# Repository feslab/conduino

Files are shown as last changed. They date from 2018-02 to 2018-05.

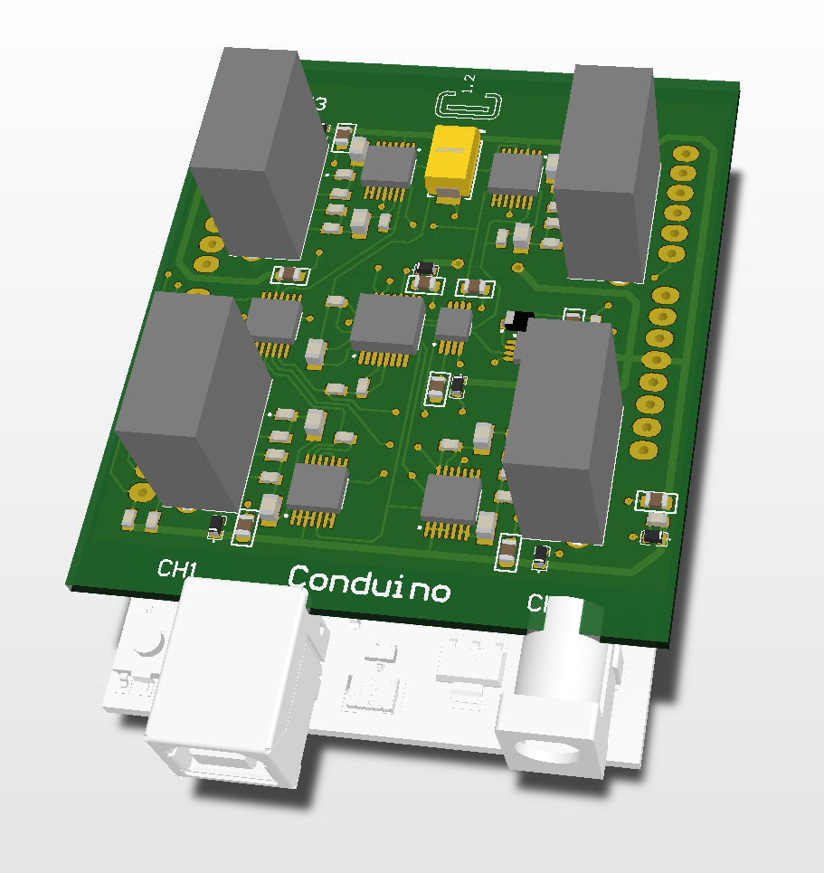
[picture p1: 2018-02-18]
hardware/Cond2.png

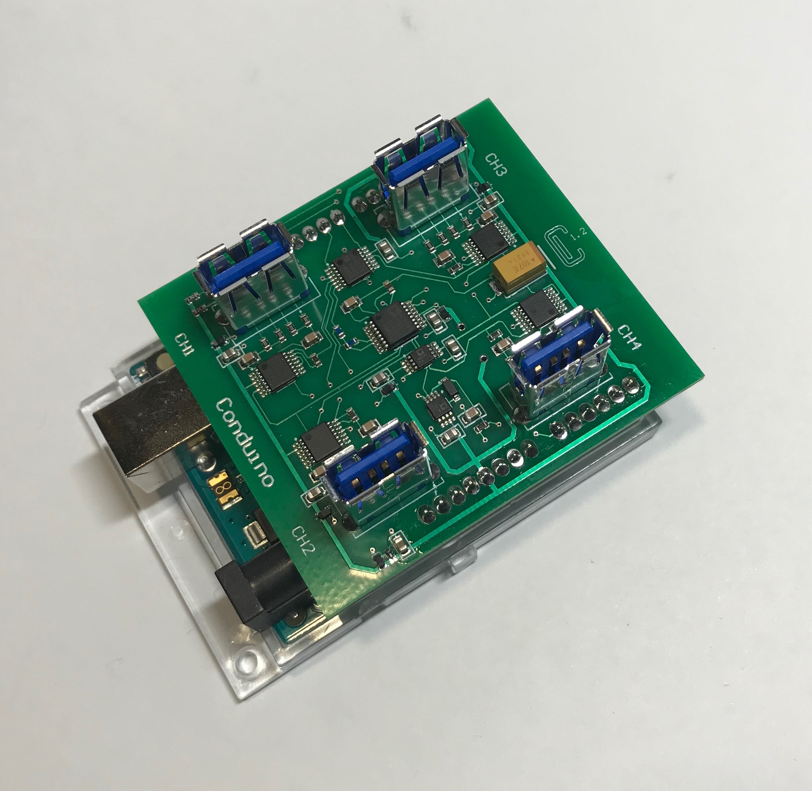
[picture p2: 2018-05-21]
hardware/AssemblyPic2.jpg

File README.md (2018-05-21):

# Conduino 1.2

For any questions or comments please contact 
[Marco Carminati](http://www.deib.polimi.it/eng/people/details/126878) or [Paolo Luzzatto-Fegiz](https://feslab.me.ucsb.edu/people/paolo-luzzatto-fegiz) 

If you use a Conduino in your work, please include the citation:
Marco Carminati, Paolo Luzzatto-Fegiz, Conduino: Affordable and high-resolution multichannel water conductivity sensor using micro USB connectors, In Sensors and Actuators B: Chemical, Volume 251, 2017, Pages 1034-1041, ISSN 0925-4005, https://doi.org/10.1016/j.snb.2017.05.184.

The repository contains the following files:

Hardware:

- Conduino_Gerber:  Gerber-format design files to prepare a PCB;
- AssemblyFile.png: Assembly overview;
- Cond1.png, Cond2.png: 3D (approximate) drawings of completed Conduino 1.2;
- Schematic Conduino 1.2.pdf: Schematics for the electronic design;
- BOM_PartType-Conduino.xlsx: Bill of materials;
- License.md: CC BY 4.0 license description.

Software:

- Matlab: Files for operation through a Matlab Script;
    - Firmware_Conduino_Matlab: Arduino Sketch;
    - ConduinoMultichannel.m: Marlab script, suitable for both Mac or PC;
- Terminal: Files for operation through a serial port terminal;
    - Firmware_Conduino_Terminal: Arduino Sketch;
    - Termite.exe: RS232 serial port terminal for PC, requires no installation see https://www.compuphase.com/software_termite.htm;
    - termite.cat: place in the same folder as Termite.exe;
    - Settings Termite.pdf: Settings for Termite, or similar serial port terminals.
- _Software_for_older_Conduinos_1p0-1p1: versions for older Conduinos;

Conduino 1.2 differs from the Conduino 1.0 described in the 2017 paper:

- Parts that were needed exclusively for the 4-electrode circuit have been removed. This revision substantially simplifies probe design, and reduces complexity. In our tests so far there has been no need to switch from 2-electrode to 4-electrode measurement;
- The overall layout has been revised for a more compact design, and to eliminate a slight kinematic conflict between Ch.4 and the Arduino Uno's USB port.

Areas of ongoing work on Conduino 1.2:

- There is currently no enclosure design. If you design an enclosure, we would be happy to add the CAD file to this repository, of course with attribution;
- If using more than one Conduino (that is, in applications where more than four sensors are needed) in the same tank, interference may develop. We are working to address this, most likely with a software update. There are no interference issues between the four sensors operated by a single Conduino.

If you are looking for an assembled system for purchase, please contact conduino@gmail.com.

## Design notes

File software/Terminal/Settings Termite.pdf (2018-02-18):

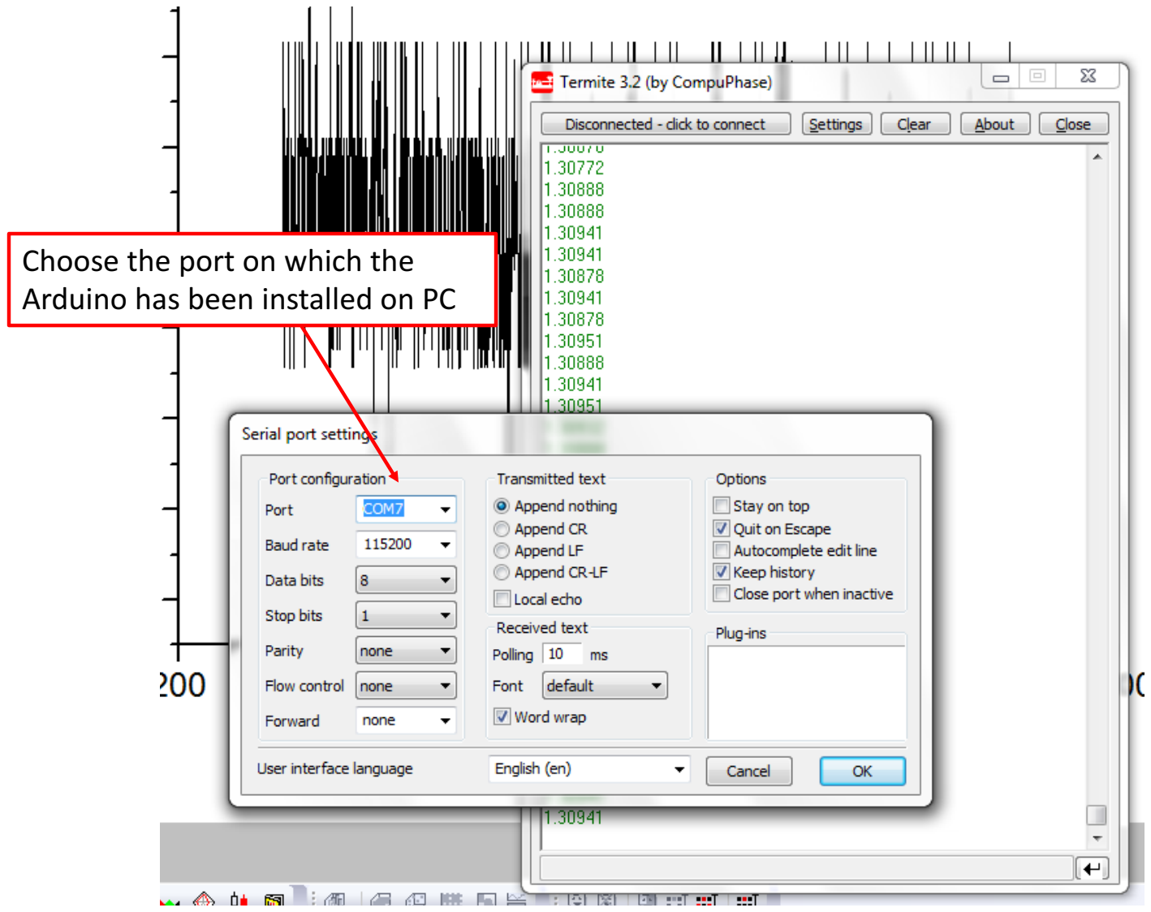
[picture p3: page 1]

Choose the port on which the Arduino has been installed on PC

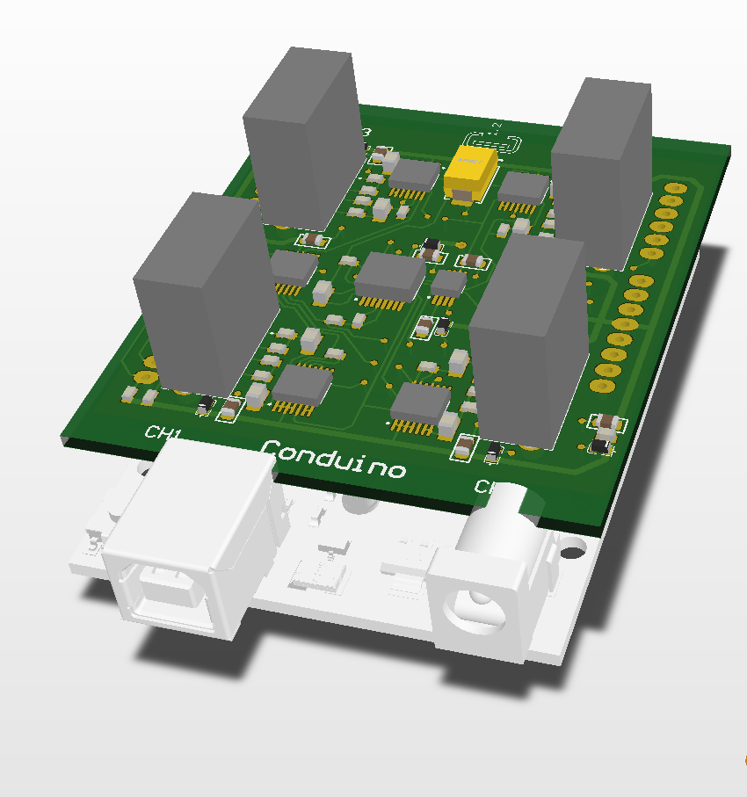
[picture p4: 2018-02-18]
hardware/Cond1.png

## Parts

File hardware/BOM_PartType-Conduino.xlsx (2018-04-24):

Designator | Comment | Quantity | Description | Manufacturer | Manufacturer PN (w. link) | Case/Package | Unitary cost | Tot cost
C1, C4, C7, C12, C17, C20, C26 | 10u | 7 | Tantalum Capacitors - Solid SMD 6.3V 10uF 20% 0603 ESR= 6 Ohms | AVX | F980J106MMA (https://www.mouser.com/ProductDetail/AVX/F980J106MMA?qs=sGAEpiMZZMuEN2agSAc2puC4lhRhLeoltAeW2dBMmdg=) | 0603 | 0.72 | 5.04
C2, C5, C6, C10, C13, C18, C19, C21, C23, C27 | 100n | 10 | Multilayer Ceramic Capacitors MLCC - SMD/SMT 0.1uF 50V X7R 20% 0805 Flx AEC-Q200 | Taiyo Yuden (https://www.mouser.it/taiyo-yuden) | UMJ212BB7104MGHT (https://www.mouser.it/ProductDetail/Taiyo-Yuden/UMJ212BB7104MGHT) | 0805 | 0.44 | 4.41
C3, C11, C14, C15, C16, C22, C24, C25, C28, C29 | 1u | 10 | Multilayer Ceramic Capacitors MLCC - SMD/SMT 0805 25V 1.00uF X8R 20% Soft Term | TDK (https://www2.mouser.com/tdk) | C2012X8R1E105M125AE | 0805 | 0.49 | 4.92
C8 | 100pF | 1 | Multilayer Ceramic Capacitors MLCC - SMD/SMT | Murata Electronics (https://www2.mouser.com/murataelectronics/) | GCM0335C1E101GA16D | 0603 | 0.10 | 0.10
C9 | 100u | 1 | Capacitor, Tantalum, 100 uF, +/- 10%, -55 to 125 degC, 2-Pin SMD, RoHS, Tape and Reel | AVX | TPME107K025R0045 | 7343 | 6.97 | 6.97
D1 | 1N4148 | 1 | Diodes - General Purpose, Power, Switching SMT Fast Switching Diode | Diodes Incorporeted | 1N4148WQ-7-F | SOD-123 | 0.20 | 0.20
J2, J3, J4, J5 | Connector | 4 | Recept Assy, Vertical, 4 Position, Thru-Hole, Type A USB, RoHS, Tray | TE Connectivity | 1734366-3 (https://www2.mouser.com/ProductDetail/TE-Connectivity-AMP/1734366-3) |  | 0.84 | 3.37
R1, R2, R6, R7, R8, R9, R11, R12, R16, R17, R20, R21, R22, R23, R25, R26 | 0 | 16 | Thick Film Resistors - SMD 1/10Watt 0ohms Commercial Use | Vishay | CRCW06030000Z0EBC (https://eu.mouser.com/ProductDetail/Vishay/CRCW06030000Z0EBC) | 0603 | 0.10 | 1.60
R3, R4 | 10k | 2 | Thick Film Resistors - SMD 1/10W 10K Ohm .1% 75V | Yageo | RE0603BRE0710KL (https://eu.mouser.com/ProductDetail/Yageo/RE0603BRE0710KL?qs=sGAEpiMZZMtlubZbdhIBIKyAF7UHeJ2ZIxtSvRbq3ww%3d) | 0603 | 0.36 | 0.72
R5, R10, R19, R24 | 180 | 4 | Thick Film Resistors - SMD 0603 Resistor 0.5% 50ppm 180Ohm | Panasonic | ERJ-3RBD1800V (https://www2.mouser.com/ProductDetail/Panasonic/ERJ-3RBD1800V) | 0603 | 0.12 | 0.48
R13 | 2.5k | 1 | Thin Film Resistors - SMD .5watt 2.5Kohm 25ppm 0.1% 0603 SMD | Vishay | PCAN0603E2501BST5 (https://www2.mouser.com/ProductDetail/Vishay-Thin-Film/PCAN0603E2501BST5) | 0603 | 0.94 | 0.94
R14, R15 | 20k | 2 | Thin Film Resistors - SMD .250W 20Kohms .5% 0603 25ppm Hi Power | Vishay | MCT0603PD2002DP500 (https://www2.mouser.com/ProductDetail/Vishay-BC-Components/MCT0603PD2002DP500) | 0603 | 0.57 | 1.14
R18 | 1k | 1 | Thick Film Resistors - SMD 0603 Resistor 0.5% 50ppm 1.1KOhm | Panasonic | ERJ-3RBD1101V (https://www2.mouser.com/ProductDetail/Panasonic/ERJ-3RBD1101V) | 0603 | 0.12 | 0.12
U1, U3, U6, U8 | Op amp | 4 | 3 Channel Single-Supply Operation Operational Amplifier, 220 MHz BW, 170 V/us SR, Industrial, 14-pin SOP (RU-14), Tube | Analog Devices | ADA4891-3ARUZ-R7 (https://www2.mouser.com/ProductDetail/Analog-Devices/ADA4891-3ARUZ-R7?qs=sGAEpiMZZMv9Q1JI0Mo%2ftbQOvCFTKx7r) | TSSOP | 2.55 | 10.20
U2 | Voltage reg. | 1 | Ultralow Noise, LDO XFET Voltage Reference with Current Sink and Source, 2.5 V Output, 3 to 18 V Supply, Industrial, 8-pin SOP (RM-8), Tube | Analog Devices | ADR441ARMZ-REEL7 | MSOP | 6.25 | 6.25
U4 | Imp measure | 1 | 1 MSPS, 12-Bit Impedance Converter, Network Analyzer, Serial, RS-16, 77 Tube, Pb-Free | Analog Devices | AD5933YRSZ | SSOP | 33.64 | 33.64
U5 | Mux | 1 | 1 pC Charge Injection, 100 pA Leakage CMOS 3 V / 5 V / +/-5 V 4-Channel Multiplexer, -40 to 125 degC, 14-pin SOP (RU-14), Tube | Analog Devices | ADG604YRUZ-REEL7 (https://www2.mouser.com/ProductDetail/Analog-Devices/ADG604YRUZ-REEL7) | TSSOP | 4.96 | 4.96
U7 | Op amp | 1 | Single Channel Rail-to-Rail Operational Amplifier, 1.9 MHz BW, 3 V/us SR, Industrial, 8-pin SOP (RM-8), Tube | Analog Devices | AD820ARMZ-R7 (https://www2.mouser.com/ProductDetail/Analog-Devices/AD820ARMZ-R7?qs=sGAEpiMZZMv9Q1JI0Mo%2ftYvoW7ReYAMC) | MSOP | 4.80 | 4.80
 |  |  |  |  |  |  | TOT | 89.87

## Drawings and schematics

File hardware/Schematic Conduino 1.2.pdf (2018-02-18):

Arduino | Channel1 | Channel2

# Channel

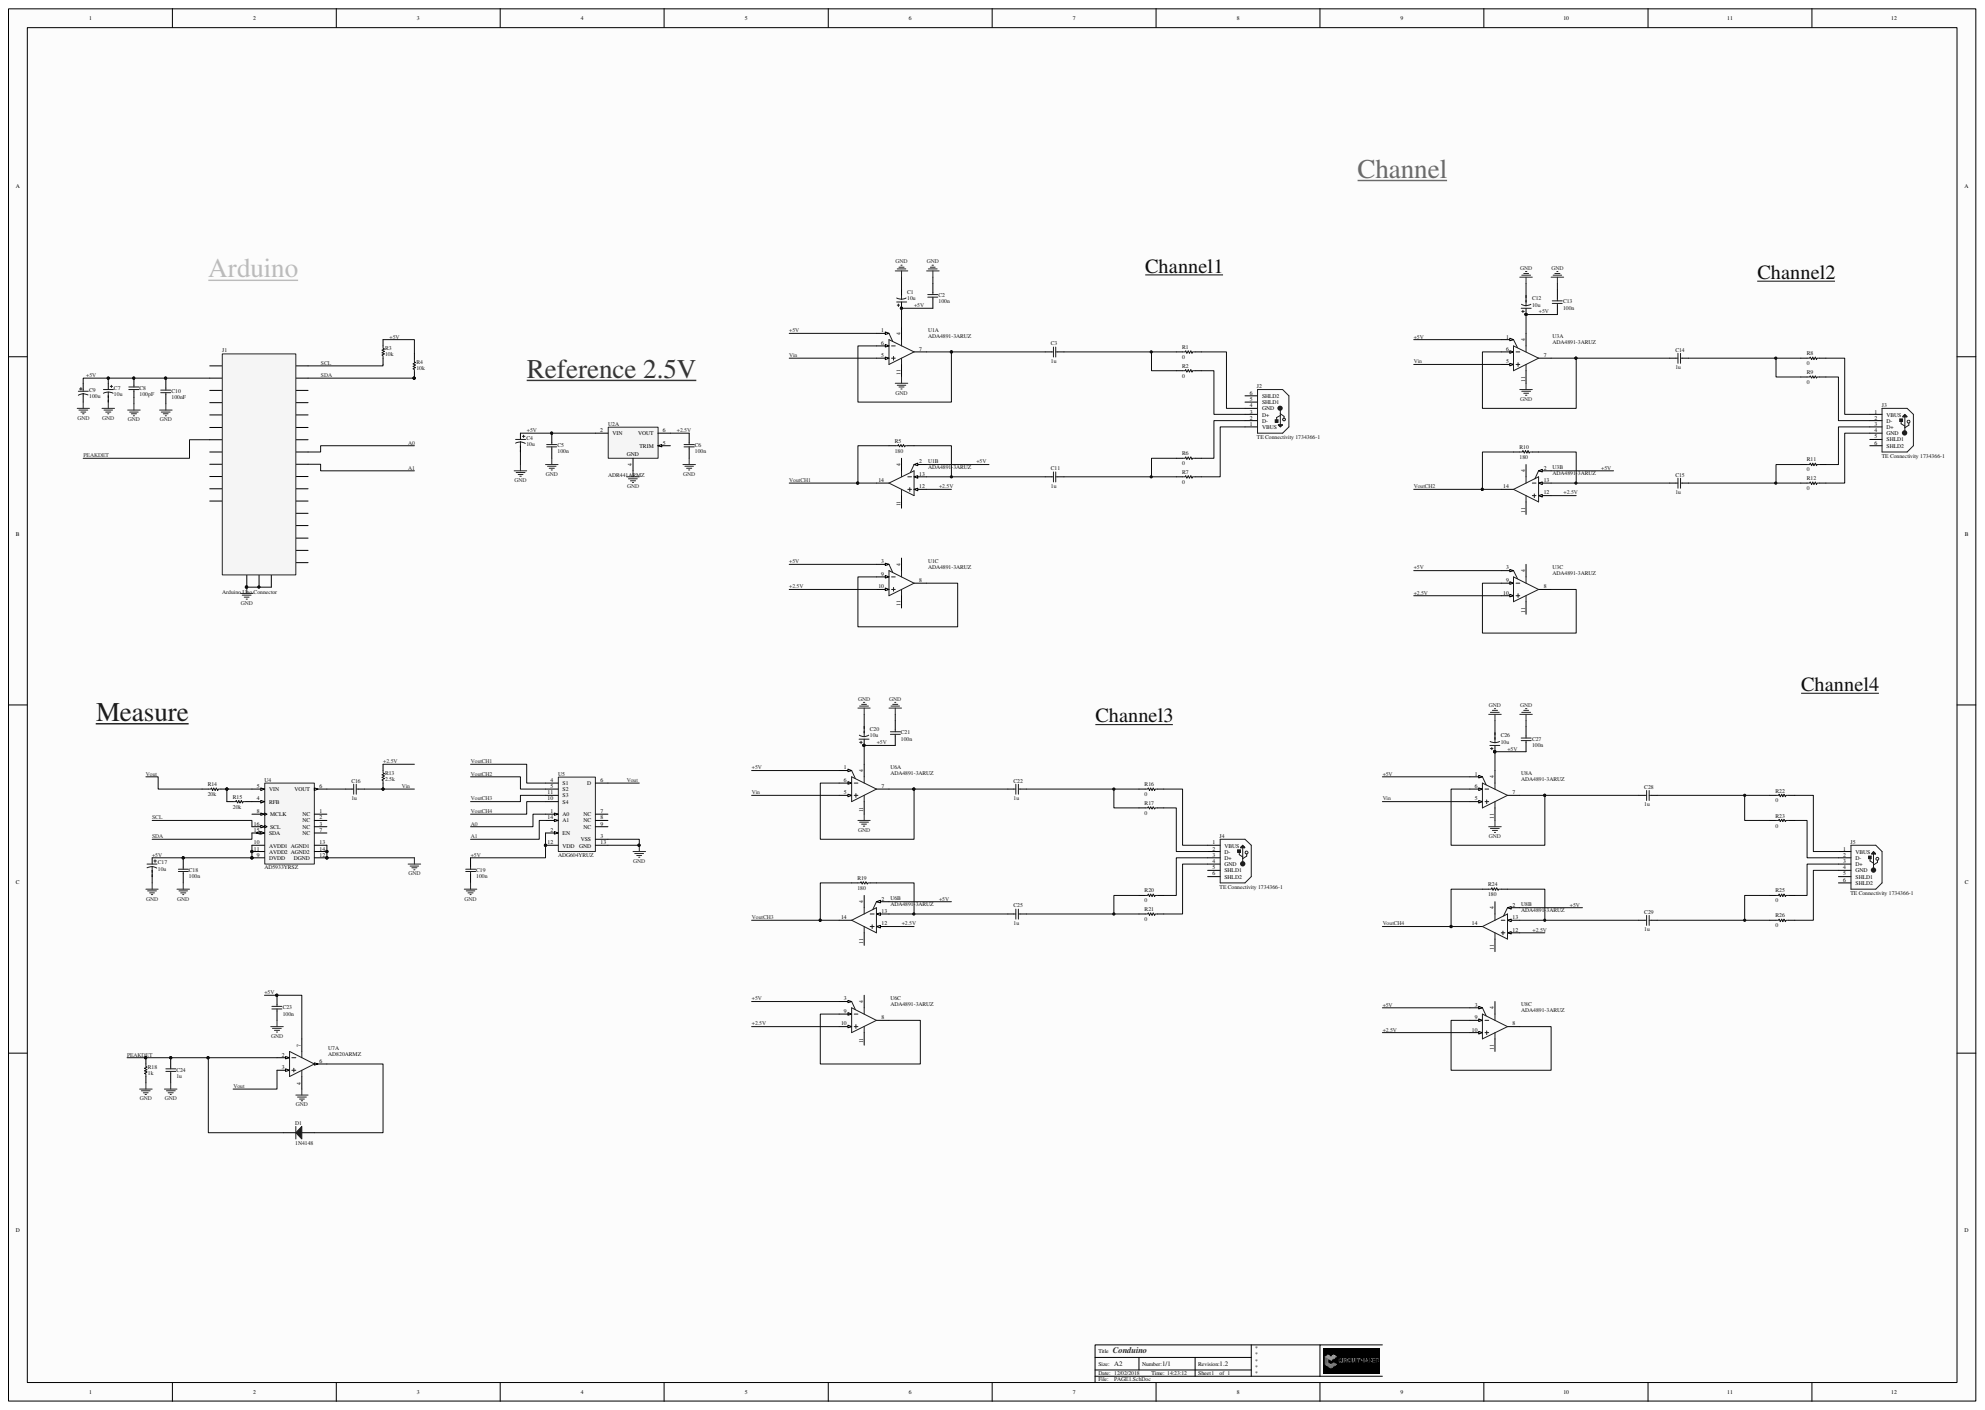
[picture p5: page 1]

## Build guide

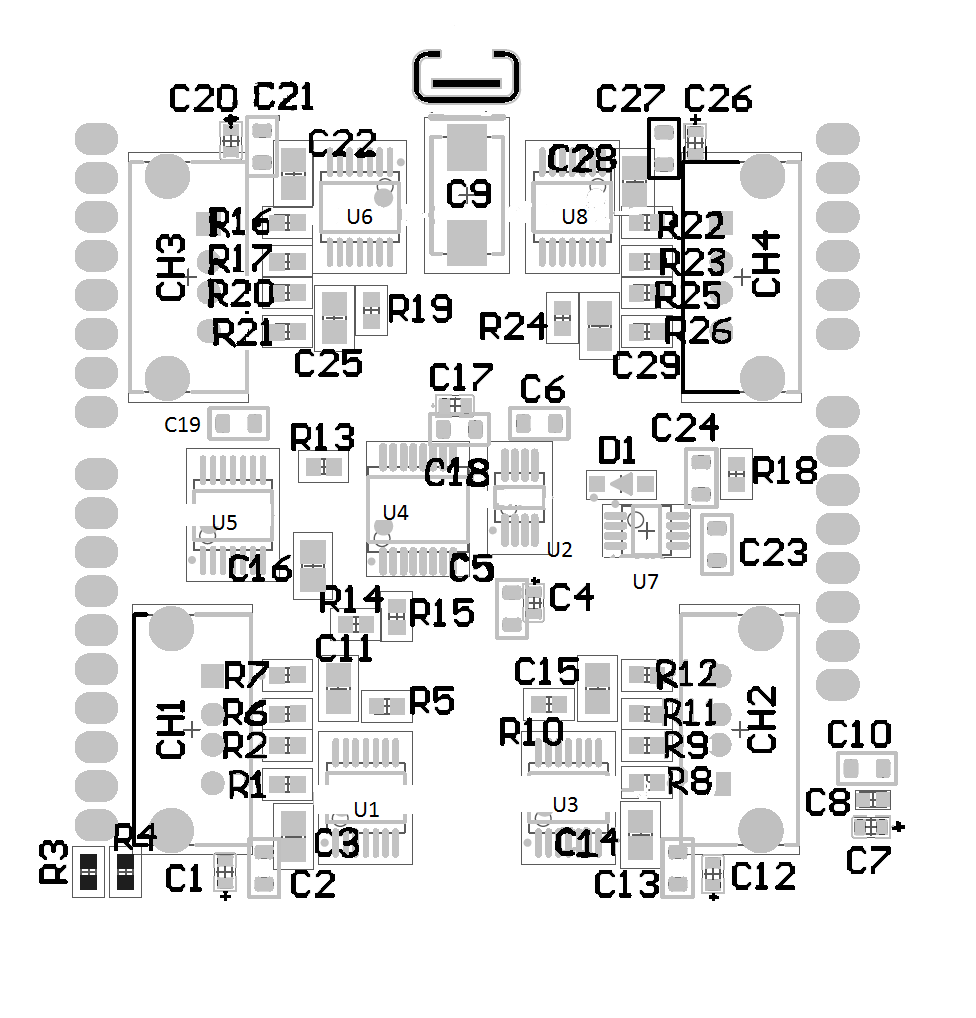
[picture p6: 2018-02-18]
hardware/Assemblyfile.png

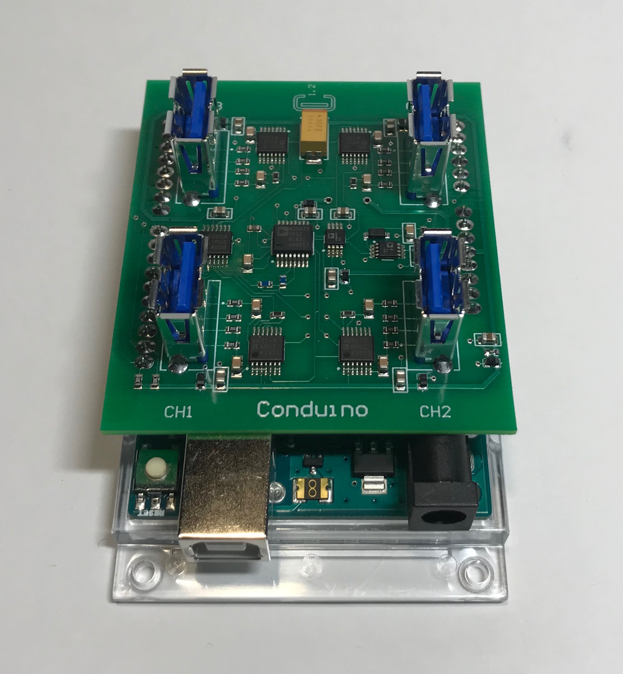
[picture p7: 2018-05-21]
hardware/AssemblyPic1.jpg

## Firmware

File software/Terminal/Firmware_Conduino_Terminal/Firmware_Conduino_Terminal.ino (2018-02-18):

#include <Wire.h>

// The user must calibrate the AD5933 system for a known impedance range to determine the gain factor

#define AD5933_ADDR 0x0D
#define AD5245_ADDR 0x2D //B0101101; // << assumes AD0 tied to VCC

const float CLOCK_SPEED = 16.776 * pow(10, 6); // AD5933 has internal clock of 16.776 MHz

const int CONTROL_REGISTER[2] =                    { 0x80, 0x81       }; // see mapping below
const int START_FREQUENCY_REGISTER[3] =            { 0x82, 0x83, 0x84 }; // 24 bits for start frequency
const int FREQ_INCREMENT_REGISTER[3] =             { 0x85, 0x86, 0x87 }; // 24 bits for frequency increment
const int NUM_INCREMENTS_REGISTER[2] =             { 0x88, 0x89       }; //  9 bits for # of increments
const int NUM_SETTLING_CYCLES_REGISTER[2] =        { 0x8A, 0x8B       }; //  9 bits + 1 modifier for # of settling times
const int STATUS_REGISTER[1] =                     { 0x8F             }; // see mapping below
const int TEMPERATURE_DATA_REGISTER[2] =     { 0x92, 0x93       }; // 16-bit, twos complement format
const int REAL_DATA_REGISTER[2] =                  { 0x94, 0x95       }; // 16-bit, twos complement format
const int IMAG_DATA_REGISTER[2] =                  { 0x96, 0x97       }; // 16-bit, twos complement format

// control register map (D15 to D12)
const int DEFAULT_VALUE =                 B0000; // initial setting
const int INITIALIZE =                    B0001; // excite the unknown impedance initially
const int START_SWEEP =             B0010; // begin the frequency sweep
const int INCREMENT =                     B0011; // step to the next frequency point
const int REPEAT =                        B0100; // repeat the current frequency point measurement
const int MEASURE_TEMP =                  B1001; // initiates a temperature reading
const int POWER_DOWN =                    B1010; // VOUT and VIN are connected internally to ground
const int STANDBY =                       B1011; // VOUT and VIN are connected internally to ground

const int BLOCK_WRITE = B1010000;
const int BLOCK_READ =  B1010001;
const int ADDRESS_PTR = 0xB0;// B1011000;

const int validTemperatureMeasurement =  1;
const int validImpedanceData =           2;
const int frequencySweepComplete =       4;

//functions declarations
int checkStatus();
boolean measureTemperature();
byte frequencyCode(float, int);
boolean setStartFrequency(float);
boolean setFrequencyIncrement(float);
boolean setNumberOfIncrements(int);
boolean setNumberOfSettlingTimes(int);
void measureImpedance();
void configureAD5933(int, float, float, int);
int getByte(int);
boolean setByte(int, int);
boolean setControlRegister(int);
void setChannel(int);

boolean setControlRegister2();


const int ledPin = 13;

int reading = 0;
byte rxByte;
int number;
char FirstChar[1];
char SecondChar[1];

int e = 0;
int y;
int ch;
int u;

// Arduino setup:

// D8 = MUX1
// D9 = MUX0


const int mux1 = 8;
const int mux0 = 9;

int channelNumber = 0;

void setup()
{
  Wire.begin();
  Serial.begin(115200);

  pinMode(ledPin, OUTPUT);

  pinMode(mux1, OUTPUT);
  pinMode(mux0, OUTPUT);


  configureAD5933(2, // number of settling times
                  1 * pow(10, 5), // start frequency (Hz)
                  1 * pow(10, 4), // frequency increment (Hz)
                  0); // number of increments

  setControlRegister2();

}

void loop()
{
      y = 2;
      Serial.print("Specify number of samples:    ");
      Serial.setTimeout(10);
      
          while (y == 2) {

              if (Serial.available()) {
                y = 1;
               number = Serial.parseInt();
               Serial.println(number);
              }
           }
          
      Serial.println("Start reading..............");
      Serial.println(" ");
      Serial.println("  Ch1               Ch2               Ch3               Ch4  ");
      digitalWrite(ledPin, HIGH);
      delay(10);

      measureImpedance();

      digitalWrite(ledPin, LOW);
      delay(1000);
}







// message sequence:
// to set the memory address:
// 1. slave address
// 2. pointer command
// 3. register address to point to

// to write data (address already set):
// 1. slave address
// 2. block write
// 3. number bytes write
// 4. byte 0, byte 1, byte 2, etc.

// to read data (address is already set):
// 1. slave address with read bit high
// 2. register data is returned

// to read a block of data (address is already set):
// 1. slave address
// 2. block read
// 3. number of bytes
// 4. slave address (read bit high)
// 5. byte 0, byte 1, byte 2, etc.


// control register map (D10 to D9)
// ranges = {2.0 V p-p, 200 mV p-p, 400 mV p-p, 1.0 V p-p}
const int OUTPUT_VOLTAGE[4] = {
  B00, B01, B10, B11
};

// control register map (D11, D8 to D0)
// D11 = no operation
// D8 = PGA gain (0 = x5, 1 = x1) // amplifies the response signal into the ADC
// D7 = reserved, set to 0
// D6 = reserved, set to 0
// D5 = reserved, set to 0
// D4 = reset // interrupts a frequency sweep
// D3 = external system clock, set to 1; internal system clock, set to 0
// D2 = reserved, set to 0
// D1 = reserved, set to 0
// D0 = reserved, set to 0

// number of increments register
// 0x88: D15 to D9 -- don't care
// 0x89: D8 -- number of increments bit 1
// 0x89: D7 to D0 -- number of increments bits 2 through 9; 9-bit integer number stored in binary format

// number of settling times
// 0x8A: D15 to D11 -- don't care
// 0x8A: D10 to D9 -- 2-bit decode
//        0 0 = default
//        0 1 = # of cycles x 2
//        1 0 = reserved
//        1 1 = # of cycles x 4
// 0x8A: D8 -- MSB number of settling times
// 0x8B: D7 to D0 -- number of settling times; 9-bit integer number stored in binary format

// status register


int checkStatus() {
  return (getByte(STATUS_REGISTER[0]) & 7);
}

boolean measureTemperature() {

  setControlRegister(MEASURE_TEMP);

  delay(10); // wait for 10 ms

  if (checkStatus() & 1 == validTemperatureMeasurement) {

    // temperature is available
    int temperatureData = getByte(TEMPERATURE_DATA_REGISTER[0]) << 8;
    temperatureData |= getByte(TEMPERATURE_DATA_REGISTER[1]);
    temperatureData &= 0x3FFF; // remove first two bits

    if (temperatureData & 0x2000 == 1) { // negative temperature

      temperatureData -= 0x4000;
    }

    temperatureData /= 32;

    Serial.print("Current temperature is ");
    Serial.print(temperatureData);
    Serial.println(" degrees Celsius.");

    setControlRegister(POWER_DOWN);

    return true;

  } else {
    return false;
  }
}

// start frequency and frequency increment formula:
byte frequencyCode(float freqInHz, int byteNum)
{
  long value = long((freqInHz / (CLOCK_SPEED / 4)) * pow(2, 27));

  byte code[3];

  code[0] = (value & 0xFF0000) >> 0x10;
  code[1] = (value & 0x00FF00) >> 0x08;
  code[2] = (value & 0x0000FF);

  return code[byteNum];
}

boolean setStartFrequency(float freqInHz)
{



  boolean statusValue;

  for (int n = 0; n < 3; n++) {
    statusValue = setByte(START_FREQUENCY_REGISTER[n], frequencyCode(freqInHz, n));
  }

  return statusValue;

}


boolean setFrequencyIncrement(float freqInHz)
{


  boolean statusValue;

  for (int n = 0; n < 3; n++) {
    statusValue = setByte(FREQ_INCREMENT_REGISTER[n], frequencyCode(freqInHz, n));
  }

  return statusValue;

}


boolean setNumberOfIncrements(int n)
{


  boolean i2cStatus;

  int numIncrements = min(n, 511);

  i2cStatus = setByte(NUM_INCREMENTS_REGISTER[0], numIncrements >> 8);
  i2cStatus = setByte(NUM_INCREMENTS_REGISTER[1], numIncrements & 255);

  return i2cStatus;
}


boolean setNumberOfSettlingTimes(int n)
{



  int decode;
  int numSettlingTimes = min(n, 2047);

  if (n > 1023) {
    decode = 3;
    numSettlingTimes /= 4;
  }
  else if (n > 511) {
    decode = 1;
    numSettlingTimes /= 2;
  }
  else {
    decode = 0;
    numSettlingTimes = n;
  }

  boolean i2cStatus;

  i2cStatus = setByte(NUM_SETTLING_CYCLES_REGISTER[0], (numSettlingTimes >> 8) + (decode << 1));
  i2cStatus = setByte(NUM_SETTLING_CYCLES_REGISTER[0], numSettlingTimes & 255);

  return i2cStatus;

}



void measureImpedance() {


  int real = 0;
  int imag = 0;
  e = 0;
  //0.Inizialize bit D11,D10,D9,D8
  setControlRegister2();

  // 1. place AD5933 in standby mode
  setControlRegister(STANDBY);

  // 2. initialize with start frequency
  setControlRegister(INITIALIZE);


  // 3. start frequency sweep
  setControlRegister(START_SWEEP);

  int rxcontrol = getByte(CONTROL_REGISTER[0]);

      real = getByte(REAL_DATA_REGISTER[0]) << 8;
      real |= getByte(REAL_DATA_REGISTER[1]);
    
        imag = getByte(IMAG_DATA_REGISTER[0]) << 8;
        imag |= getByte(IMAG_DATA_REGISTER[1]);
    

  // start array:



  // 4. poll status register until complete
  //while (checkStatus() < validImpedanceData) {
  //}
  for (u = 0; u < number; u++) { 
    
    for ( ch=1; ch < 5 ; ch++) {

      setChannel(ch);
    setControlRegister(REPEAT);
      delay(6);

      // 5. read values
      real = getByte(REAL_DATA_REGISTER[0]) << 8;
      real |= getByte(REAL_DATA_REGISTER[1]);

        if (real > 0x7FFF) { // negative value
          real &= 0x7FFF;
          real -= 0x10000;
        }
    
        imag = getByte(IMAG_DATA_REGISTER[0]) << 8;
        imag |= getByte(IMAG_DATA_REGISTER[1]);
    
        if (imag > 0x7FFF) { // negative value
          imag &= 0x7FFF;
          imag -= 0x10000;
        }
    
        double magnitude = sqrt(pow(double(real), 2) + pow(double(imag), 2));
        double gain = 2.3 * pow(10, -10); //calibrated with 220kOhm resistor on 1/3/12
    
        double impedance = 1 / (gain * magnitude * 45400 / 1.63);
    
        double phase = atan(double(imag) / double(real)) * 360 / (2 * 3.14) + 47;
    
        double conductivity = 129 / impedance;
    
    
        //Serial.print("Conductivity: ");
        Serial.print(conductivity, 4);
        Serial.print("            ");
    
    
        //  double limit = analogRead(A0);
        //   limit *=5;
        //   limit /=1023;
        //   Serial.print(limit);
        //   Serial.print(" V ");
        //   Serial.println("; ... ");
    
    
    
    
        //Serial.println(" ");


  }
  Serial.println(" ");
  }




  // 8. power-down mode
  setControlRegister(POWER_DOWN);


}


void configureAD5933(int settlingTimes, float startFreq, float freqIncr, int numIncr)
{
  setNumberOfSettlingTimes(settlingTimes);
  setStartFrequency(startFreq);
  setFrequencyIncrement(freqIncr);
  setNumberOfIncrements(numIncr);

}






// How to write or read a byte:
// 1. master device asserts a start condition on SDA
// 2. master sends the 7-bit slave address followed by the write bit (low)
// 3. addressed slave device asserts an acknowledge on SDA
// 4. The master send a register address or pointer command code (1011 0000)
// 5. the slave asserts an acknowledge on SDA
// 6. the master sends a data byte or register address to where the pointer is to point
// 7. the slave asserts an acknowledge on SDA
// 8. the master asserts a stop condition on SDA to end the transaction

int getByte(int address) {

  int rxByte;

  Wire.beginTransmission(AD5933_ADDR);
  Wire.write(ADDRESS_PTR);
  Wire.write(address);
  int i2cStatus = Wire.endTransmission();

  Wire.requestFrom(AD5933_ADDR, 1);

  if (1 <= Wire.available()) {
    rxByte = Wire.read();
  }
  else {
    rxByte = -1;
  }

  return rxByte;

}

boolean setByte(int address, int value) {

  Wire.beginTransmission(AD5933_ADDR);
  Wire.write(address);
  Wire.write(value);
  int i2cStatus = Wire.endTransmission();

  if (i2cStatus)
    return false;
  else
    return true;

}

boolean setControlRegister(int code) {

  int rxByte = getByte(CONTROL_REGISTER[0]);

  rxByte &= 0x0F; // clear upper four bits
  rxByte |= code << 4; // set to 1011

  boolean s = setByte(CONTROL_REGISTER[0], rxByte);

  delay(1);


  return s;

}
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

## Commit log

2018-02-18 Hardware version 1.2
    [BOM_PartType-Conduino.xlsx, PCB2.GBL, PCB2.GBS, PCB2.GTL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]
2018-04-24 Delete BOM_PartType-Conduino.xlsx
    BOM Updated to reflect component availability.
    [BOM_PartType-Conduino.xlsx]
2018-04-24 Updated to use in-stock components
    [BOM_PartType-Conduino.xlsx]
2018-05-07 Switched Gerber folder to zip
    [PCB2.GTL, PCB2.GTO, PCB2.GTS]
2018-05-17 Pic of assembly added
2018-05-21 Added assembly pictures
